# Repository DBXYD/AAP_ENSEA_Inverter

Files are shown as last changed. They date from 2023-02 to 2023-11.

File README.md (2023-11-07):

# ENSEA - Projet Onduleur Triphasé didactique, 60V, 10A
- Rédaction : Nicolas Papazoglou, Alexis Martin,
- Desgin et Réalisation : Nicolas Papazoglou, Alexis Martin, Patricia Kittel,
- Conseils : Pierre Toussaint.

# Présentation du projet

## Motivations
Dans le cadre de la formation des étudiants de l'ENSEA, les professeurs ont ressenti le besoin de créer une maquette pédagogique pour plusieurs raisons : 
* De nombreuses pannes récurentes sur les maquettes existantes,
* Réparations chronophages voir impossibles,
* L'ensemble du matériel est caché des étudiants, ils ne peuvent pas voir l'intérieur, le routage de la carte et les composants,
* Le coût de l'ensemble du matériel acheté est important.

## Objectifs
* Réalisation d'une maquette fiable pour les TPs d’électrotechnique et automatique : Gain en temps et en autonomie pour les étudiants,
* Feedback automatique en fonction des erreurs détectées : Gain en autonomie pour les étudiants, possibilité de travail hors séance sans
supervision d’un professeur,
* Projet open-source (disponible sur github),
* Compréhension globale possible par les étudiants, application de l’ensemble de leurs cours dans une maquette,
* Création modulaire, réutilisable dans d’autres cours/projets,
* Evolution possible à d’autres enseignements (buck/boost, 4Q, brushless, moteurs synchrones, asservissement, etc...),
* Maintenance facile et rapide

## Cahier des charges
* Onduleur triphasé 60V / 15A,
* Protections surtensions et surintensités,
* Commande de mise sous tension,
* Pilotage par liaison UART over USB,
* Utilisable en commande “brushless” : entrées position “hall” ,
* Utilisable en commande vectorielle ou MCC : entrée position “encoder”,
* Protection alimentation non réversible : module “freinage”,
* Vérification automatique des temps morts,
* Mesure de courants (hall) dans les 3 phases + entrée,
* Mesure de tension dans les 3 phases + entrée,
* Alimentation externe secteur,
* Affichage erreurs, intensité PWM (affiche externe),
* Sorties mesures de courants et PWMs,
* Boitier,
* Tenue thermique,
* Isolation galvanique.

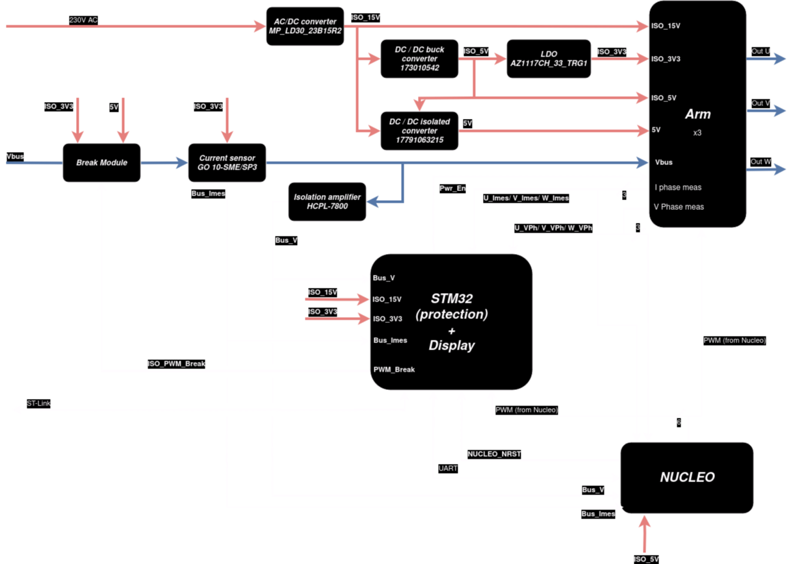
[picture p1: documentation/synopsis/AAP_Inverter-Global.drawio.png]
synopsis


# Guide d'utilisation

# Guide du développeur
La majorité des signaux sont disponibles sur les connecteurs morpho au format des cartes Nucleo-64.
Sur la base des cartes Nucleo, les connecteurs répérés CN7 et CN10 sont disponibles pour intégrer une carte custom.

## Connecteurs
### Connecteur CN7
| Type           | Label         | Pin number | Pin number | Label         | Type           |
|----------------|---------------|------------|------------|---------------|----------------|
| Digital Output | UART_TX_STM32 | 1          | 2          | UART_RX_STM32 | Digital Input  |
|                | N.C.          | 3          | 4          | NRST_STM32    | Digital Output |
|                | N.C.          | 5          | 6          | 5V            | Power Input    |
|                | N.C.          | 7          | 8          | GND           | Power Input    |
|                | N.C.          | 9          | 10         | N.C           |                |
|                | N.C.          | 11         | 12         | N.C           |                |
|                | N.C.          | 13         | 14         | N.C.          |                |
|                | N.C.          | 15         | 16         | N.C.          |                |
|                | N.C.          | 17         | 18         | N.C.          |                |
| Power Input    | GND           | 19         | 20         | GND           | Power Input    |
|                | N.C.          | 21         | 22         | GND           | Power Input    |
|                | N.C.          | 23         | 24         | N.C.          |                |
|                | N.C.          | 25         | 26         | N.C.          |                |
|                | N.C.          | 27         | 28         | Bus_V         | Analog Input   |
|                | N.C.          | 29         | 30         | U_Imes        | Analog Input   |
|                | N.C.          | 31         | 32         | Enc_B         | Digital Input  |
|                | N.C.          | 33         | 34         | W_Imes        | Analog Input   |
| Analog Input   | Bus_Imes      | 35         | 36         | W_Vph         | Analog Input   |
| Analog Input   | V_Vph         | 37         | 38         | U_Vph         | Analog Input   |

### Connecteur CN10
| Type           | Label         | Pin number |            | Label         | Type           |
|----------------|---------------|------------|------------|---------------|----------------|
|                | N.C.          | 1          | 2          | Enc_Z         | Digital Input  |
|                | N.C.          | 3          | 4          | N.C.          |                |
|                | N.C.          | 5          | 6          | N.C.          |                |
|                | N.C.          | 7          | 8          | N.C.          |                |
| Power Input    | GND           | 9          | 10         | N.C.          |                |
|                | N.C.          | 11         | 12         | N.C.          |                |
| Digital Input  | Enc_A         | 13         | 14         | N.C.          |                |
|                | N.C.          | 15         | 16         | N.C.          |                |
|                | N.C.          | 17         | 18         | N.C.          |                |
|                | N.C.          | 19         | 20         | GND           | Power Input    |
| Output         | V_PWM_H       | 21         | 22         | N.C.          |                |
| Output         | U_PWM_H       | 23         | 24         | V_Imes        | Analog Input   |
|                | N.C.          | 25         | 26         | W_PWM_L       | Output         |
|                | N.C.          | 27         | 28         | V_PWM_L       | Output         |
|                | N.C.          | 29         | 30         | U_PWM_L       | Output         |
|                | N.C.          | 31         | 32         | GND           | Power Input    |
| Output         | W_PWM_H       | 33         | 34         | N.C.          |                |
|                | N.C.          | 35         | 36         | N.C.          |                |
|                | N.C.          | 37         | 38         | N.C.          |                |

## Input / Output labels

### Communication avec le micro-controleur présent sur la carte-mère
* UART_TX_STM32 : UART vers le micro-controleur
* UART_RX_STM32 : UART depuis le micro-controleur
* NRST_STM32 : signal pour faire un reset du micro-controleur de la carte

### Communication avec le module encodeur
* Enc_A : entrée du signal A de l'encodeur
* Enc_B : entrée du signal B de l'encodeur
* Enc_Z : entrée du signal Z de l'encodeur

### Mesure de tension
* Bus_V : mesure de la tension du bus d'alimentation
* U_Vph : mesure de la tension de la sortie U (entre les 2 transistors)
* V_Vph : mesure de la tension de la sortie V (entre les 2 transistors)
* W_Vph : mesure de la tension de la sortie W (entre les 2 transistors)

### Mesure de courant
* Bus_Imes : mesure de courant du bus d'alimentation
* U_Imes
* V_Imes
* W_Imes

### Génération de PWM
* U_PWM_H
* U_PWM_L
* V_PWM_H
* V_PWM_L
* W_PWM_H
* W_PWM_L

# FAQ

# Pannes courantes 
## Dysfonctionnement des Mosfet
Plusieurs causes peuvent causer la destruction des transistors : 
* Non respect des temps mort,
* Commande provocant une freinage trop important : retour du courant chargeant les condensateurs sur le bus d'alimentation. Ceci provoque la montée en tension du bus au-delà des spécifications des transistor de puissance

Détection de la panne : 
* Débrancher l'ensemble des câbles de la maquette, et le cas échéant, attendre que les condensateurs du bus d'alimentation soient totalement vides.
* A l'aide d'un multimètre, en mode diode, tester la continuité entre :
  - Entre la sortie U et le bus d'alimentation (Q202)
  - Entre la sortie U et la masse (Q203)
  - Entre la sortie V et le bus d'alimentation (Q302)
  - Entre la sortie V et la masse (Q303)
  - Entre la sortie W et le bus d'alimentation (Q402)
  - Entre la sortie W et la masse (Q403)
* Le fonctionnement normal est l'absence de continuité électrique. Dans le cas d'une continuité, le transistor en question est HS, il doit donc être changé.

# Composants
* Drivers de Mosfet/optocoupleur : HCPL-315J, Optocoupleurs sortie logique 0.5A IGBT Gate Drive [link](https://www.mouser.fr/ProductDetail/Broadcom-Avago/HCPL-315J?qs=s%252BgfxR24RQ4lntGToXJAvA%3D%3D)
* Transistor MOSFET : IRF540NPBF, MOSFET de puissance, Canal N, 100 V, 33 A, 0.044 ohm, TO-220AB, Traversant [Link](https://fr.farnell.com/infineon/irf540npbf/transistor-mosfet-canal-n-to220/dp/8648298?st=irf540n)
* Capteur de Courant : GO 10-SME/SP3, Capteur de courant, 300 kHz, SOIC, 8 Broche(s), 3.135 V, 3.465 V [Link](https://fr.farnell.com/lem/go-10-sme-sp3/capteur-courant-300khz-soic-8/dp/3796461?st=GO%2010-SME/SP3)
* Power supply : MP-LD30-23B15R2 - Alimentation montage PCB AC/DC (PSU), ITE, Équipements Ménagers et Transformateurs, 1 sortie [link](https://fr.farnell.com/multicomp-pro/mp-ld30-23b15r2/power-supply-ac-dc-15v-2a/dp/3780527)
* Power regulator : Input : 5V DC, Output : 3.3V DC, AZ1117CH-3.3TRG1 - LDO, FIXE, 3,3V, 0.8A, -20 A 125°C [link](https://fr.farnell.com/diodes-inc/az1117ch-3-3trg1/ldo-fixe-3-3v-0-8a-20-a-125-c/dp/3483073RL)
* Alimentation 15V/400mA isolé : MPRB2415S-6W - Conv. DC/DC, montage traversant isolé, ITE, 4:1, 6 W, 1 sortie, 15 V, 400 mA [link](https://fr.farnell.com/multicomp-pro/mprb2415s-6w/convertisseur-dc-dc-15v-0-4a/dp/3652723)
* Alimentation 5V/200mA isolé : 17791063215 - MagI³C-VISM Variable Isolated SIP Module, [Link](https://www.we-online.com/components/products/datasheet/17791063215.pdf)
* Connector : PX0580/PC Connecteur de puissance IEC, Entrée IEC C14, 10 A, 250 VAC, Traversant [link](https://fr.farnell.com/bulgin/px0580-pc/embase-iec-c14-carte-proto-10a/dp/313853)
* Screen : MDOB128064XV-YI - OLED graphique, 128 x 64 pixels, Jaune sur noir, 3.3V, I2C, 35.5mm x 32mm, -40 °C [Link](https://fr.farnell.com/midas/mdob128064xv-yi/afficheur-oled-cob-128-x-64-pix/dp/3407293)
* Break resistor : 162-3488 - Résistance à montage sur châssis Aluminium, 5Ω 100W ±1% [Link](https://fr.rs-online.com/web/p/resistances-a-montage-sur-chassis/1623488)
* Break schottky : VS-15TQ060S-M3 - Redresseur Schottky, 60 V, 15 A, Une, TO-263AB, 3 Broche(s), 620 mV [Link](https://fr.farnell.com/vishay/vs-15tq060s-m3/diode-schottky-simple-60v-to263ab/dp/2909608?ost=2909608)

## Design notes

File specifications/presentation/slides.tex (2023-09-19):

%\documentclass[french]{beamer}
\documentclass[aspectratio=169]{beamer}
\usepackage[utf8]{inputenc}
\usepackage[T1]{fontenc}
\usepackage{lmodern}
\usepackage{amsmath, amssymb}
\usepackage{babel}

\usepackage{eurosym}
%\usepackage{unicode-math}
\setbeamertemplate{footline}[frame number]
\def\checkmark{\tikz\fill[scale=0.4](0,.35) -- (.25,0) -- (1,.7) -- (.25,.15) -- cycle;} 
\definecolor{rouge}{HTML}{DD0000}

%Pour le TITLEPAGE

\title{Appel à projet - Présentation}
\subtitle{\today}
\date{}
\author[N.P. - A.M. - P.T.]{Nicolas Papazoglou, Alexis Martin \& Pierre Toussaint}
\institute[ENSEA]{ENSEA}

\usetheme{ensea}  

\begin{document}

\begin{frame}
	\titlepage
\end{frame}

\begin{frame}{Rappel}
\begin{minipage}{0.49\textwidth}
	\begin{itemize}
		\item Porteurs du projet : Nicolas Papazoglou, Alexis Martin, Pierre Toussaint,
		\item Demande budgétaire : 64 HETD, 
		\item Budget (DEE) : 400-500\euro/maquette,
		\item Activités concernées : enseignements d'électrotechnique et d'automatique.
	\end{itemize}
\end{minipage}
\begin{minipage}{0.49\textwidth}
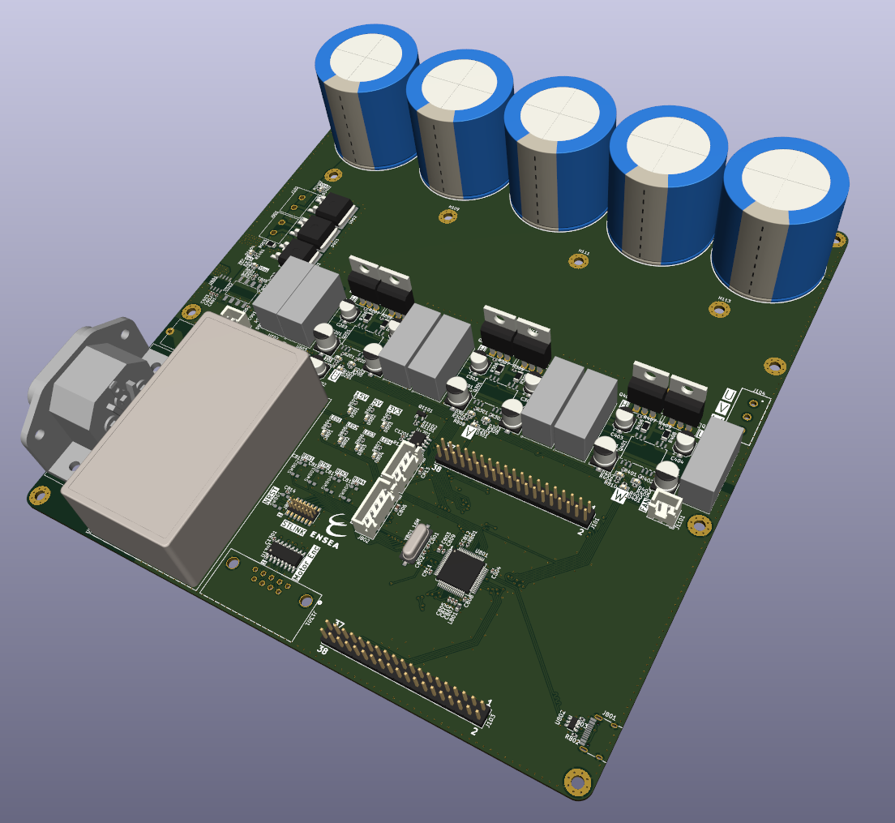
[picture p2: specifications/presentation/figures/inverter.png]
	 
\end{minipage}
\center \href{https://github.com/DBXYD/AAP_ENSEA_Inverter}{Lien github}
\end{frame}

%********************** OBJECTIFS ******************************
\begin{frame}{Contexte}
\begin{itemize}
	\item Maquette de TP : onduleur triphasé,
	\item TP en 3eme année (Enseignements d'électrotechnique et d'automatique) : 
	\begin{itemize}
	\item [ESE\_3745] Actionneur et automatique appliquée
	\item [MSC\_3805] Systèmes d'Acquision et de commande
	\end{itemize}
	\item 12 maquettes obsolète Powermodule MC1L 3-Phase (Microchip) : 
	\item Pannes récurentes :
	\begin{itemize}
		\item Perte de temps pour les étudiants,
		\item Recherche de panne et réparation par les professeurs,
		\item Boite noire pour les étudiants.		
	\end{itemize}
\end{itemize}
\end{frame}

\begin{frame}{Objectif : Réalisation maquette pédagogique}
	Objectifs : 
	\begin{enumerate}
		\item Une maquette fiable pour les TPs d'électrotechnique et automatique \\
		$\rightarrow$ Gain en temps et en autonomie pour les étudiants, \checkmark
		\item Feedback automatique en fonction des erreurs détectées, \\
		$\rightarrow$ Gain en autonomie pour les étudiants, possibilité de travail hors séance sans supervision d'un professeur,
		\item Projet open-source (disponible sur \href{https://github.com/DBXYD/AAP_ENSEA_Inverter}{github}), \checkmark
		\item Compréhension globale possible par les étudiants, application de l'ensemble de leurs cours dans une maquette, \checkmark
		\item Création modulaire, réutilisable dans d'autres cours/projets,  \checkmark
		\item Evolution possible à d'autres enseignements (buck/boost, 4Q, brushless, moteurs synchrones, asservissement, etc...), \checkmark
		\item Maintenance facile et rapide. \checkmark
	\end{enumerate}
\end{frame}

\begin{frame}{Bilan}
\begin{enumerate}
	\item Cahier des charges \checkmark,
	\item Schéma d'architecture \checkmark,
	\item Choix des composants \checkmark,
	\item Prototypage et tests unitaires électriques \checkmark,
	\item Réalisation software et tests complets (50\%),
	\item Réalisation mécanique (boitier) (50\%),
	\item Documentation (\href{https://github.com/DBXYD/AAP_ENSEA_Inverter}{github}). (80\%)
\end{enumerate}
\pause
Remarque :\begin{itemize}
	\item Coût : 300\euro/maquette,
	\item 8 cartes en fabrication dans l'immédiat
	\item Beaucoup de composants gratuits
\end{itemize}	
\end{frame}

\begin{frame}{Schematic}
\begin{center}
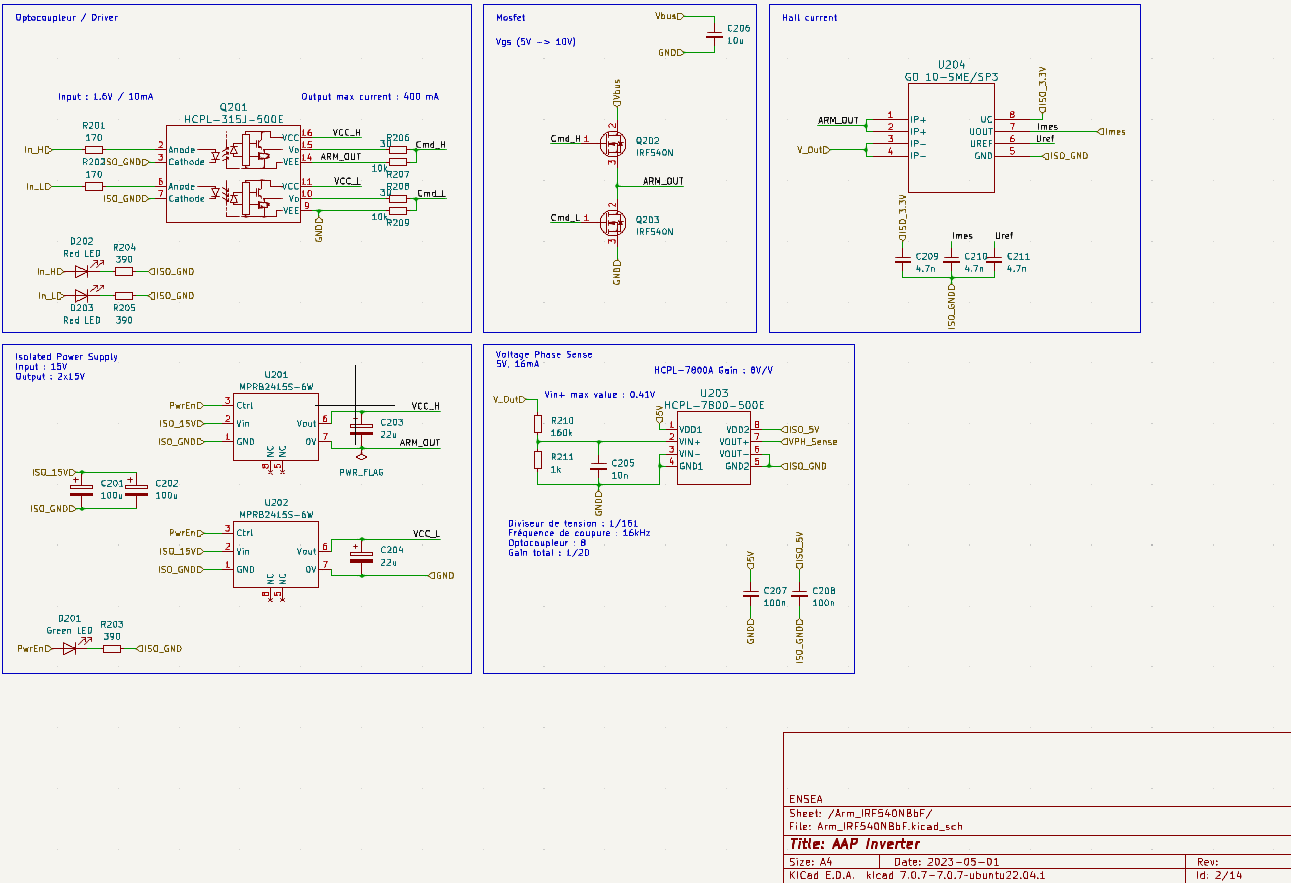
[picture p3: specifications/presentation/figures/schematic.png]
	 
\end{center}
\end{frame}

\begin{frame}{PCB}
\begin{minipage}{0.49\textwidth}
\begin{center}
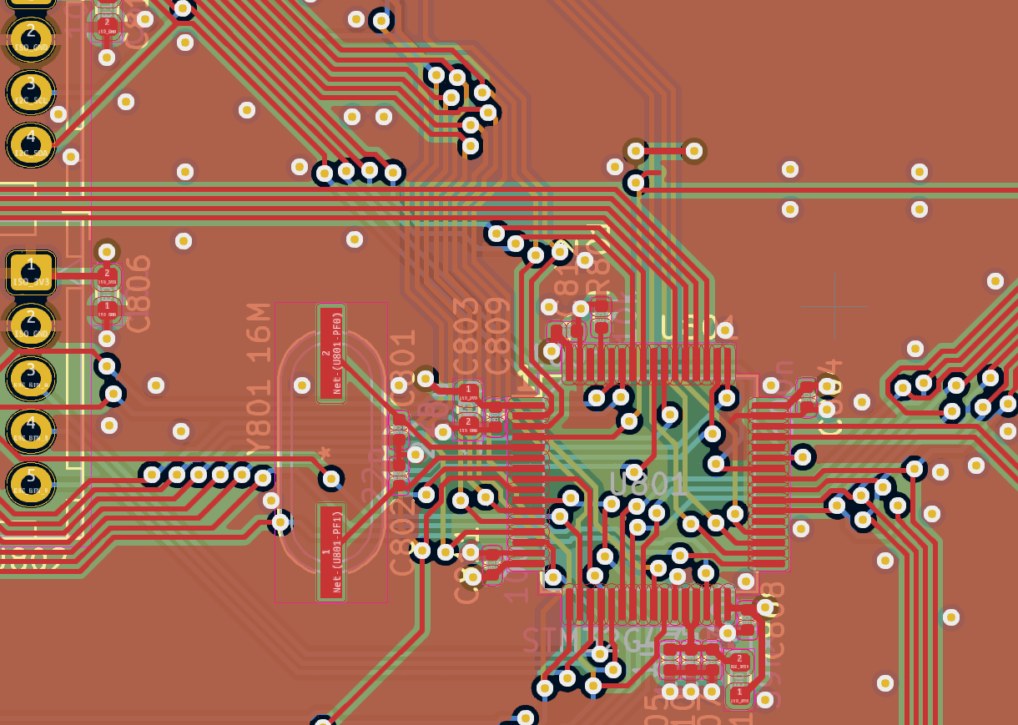
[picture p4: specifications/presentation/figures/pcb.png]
	 
\end{center}
\end{minipage}
\begin{minipage}{0.49\textwidth}
\begin{itemize}
	\item 242 composants (60 différents),
	\item 2000 segments de pistes,
	\item 906 pads
	\item 225 signaux
\end{itemize}
\end{minipage}
\end{frame}

\begin{frame}{La suite}
\begin{minipage}{0.39\textwidth}
\begin{center}
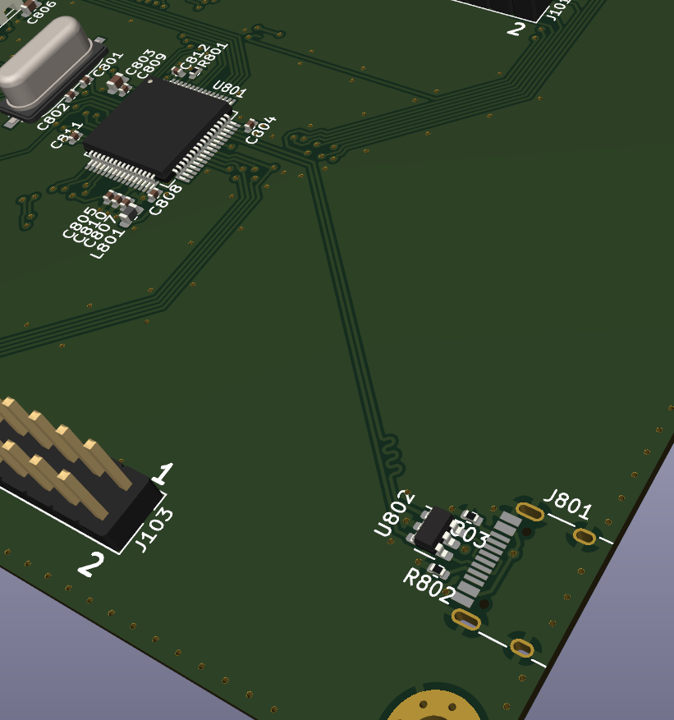
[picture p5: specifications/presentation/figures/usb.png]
	 
\end{center}
\end{minipage}
\begin{minipage}{0.59\textwidth}
Idée 1 : 
\begin{itemize}
	\item Connexion usb fonctionnelle
	\item Possibilité de récupérer toutes les données internes
	\item Programme et interface (Python) pour afficher de façon didactique l'état du moteur
\end{itemize}
Idée 2 : 
\begin{itemize}
	\item Possibilité de TP de puissance à distance
\end{itemize}
Idée 3 : 
\begin{itemize}
	\item Portage de ce projet sur d'autres cours 
	\item Carte fille différente (remplacement de la Nucléo)
\end{itemize}
\end{minipage}
\end{frame}

\end{document}

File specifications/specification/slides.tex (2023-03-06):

%\documentclass[french]{beamer}
\documentclass[aspectratio=169]{beamer}
\usepackage[utf8]{inputenc}
\usepackage[T1]{fontenc}
\usepackage{lmodern}
\usepackage{amsmath, amssymb}
\usepackage{babel}

\usepackage{eurosym}
%\usepackage{unicode-math}
\setbeamertemplate{footline}[frame number]

\definecolor{rouge}{HTML}{DD0000}

%Pour le TITLEPAGE

\title{Appel à projet}
\subtitle{Mardi 7 mars 2023}
\date{}
\author[N.P. - A.M. - P.T.]{Nicolas Papazoglou, Alexis Martin \& Pierre Toussaint}
\institute[ENSEA]{ENSEA}

\usetheme{ensea}  

\AtBeginSection[]
{
	\begin{frame}{Plan}
		\tableofcontents[currentsection]
	\end{frame}
}

\AtBeginSubsection[]
{
   \begin{frame}
    	\tableofcontents[currentsection,currentsubsection]
   \end{frame}
}

\begin{document}

\begin{frame}
	\titlepage
\end{frame}

\begin{frame}{Appel à projet}
\begin{minipage}{0.49\textwidth}
	\begin{itemize}
		\item Porteurs du projet : Alexis Martin, Nicolas Papazoglou, Pierre Toussaint,
		\item Demande budgétaire : 64 HETD,
		\item Budget (DEE) : 400-500\euro/maquette,
		\item Activités concernées : enseignements d'électrotechnique et d'automatique.
	\end{itemize}
\end{minipage}
\begin{minipage}{0.49\textwidth}
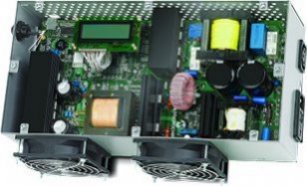
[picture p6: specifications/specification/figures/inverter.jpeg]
	 
\end{minipage}
\center \href{https://github.com/DBXYD/AAP_ENSEA_Inverter}{Lien github}
\end{frame}

%********************** OBJECTIFS ******************************
\begin{frame}{Contexte}
\begin{itemize}
	\item Maquette de TP : onduleur triphasé,
	\item TP en 3eme année (Enseignements d'électrotechnique et d'automatique) : 
	\begin{itemize}
	\item [AEI\_3121] Commande numérique directe de dispositifs
	\item [ESE\_3745] Actionneur et automatique appliquée
	\item [MSC\_3805] Systèmes d'Acquision et de commande
	\end{itemize}
	\item 12 maquettes obsolète Powermodule MC1L 3-Phase (Microchip) : 
	\item Pannes récurentes :
	\begin{itemize}
		\item Perte de temps pour les étudiants,
		\item Recherche de panne et réparation par les professeurs,
		\item Boite noire pour les étudiants.		
	\end{itemize}
\end{itemize}
\end{frame}

\begin{frame}{Objectif : Réalisation maquette pédagogique}
	Objectifs : 
	\begin{enumerate}
		\item Une maquette fiable pour les TPs d'électrotechnique et automatique \\
		$\rightarrow$ Gain en temps et en autonomie pour les étudiants,
		\item Feedback automatique en fonction des erreurs détectées, \\
		$\rightarrow$ Gain en autonomie pour les étudiants, possibilité de travail hors séance sans supervision d'un professeur,
		\item Projet open-source (disponible sur \href{https://github.com/DBXYD/AAP_ENSEA_Inverter}{github}),
		\item Compréhension globale possible par les étudiants, application de l'ensemble de leurs cours dans une maquette,
		\item Création modulaire, réutilisable dans d'autres cours/projets, 
		\item Evolution possible à d'autres enseignements (buck/boost, 4Q, brushless, moteurs synchrones, asservissement, etc...),
		\item Maintenance facile et rapide.
	\end{enumerate}
\end{frame}

\begin{frame}{Travail à effectuer}
\begin{enumerate}
	\item Cahier des charges (déjà effectué),
	\item Schéma d'architecture (déjà effectué),
	\item Choix des composants (disponibles et actuels pour une maintenibilité la plus longue possible),
	\item Prototypage et tests unitaires électriques,
	\item Réalisation software et tests complets,
	\item Réalisation mécanique (boitier),
	\item Intégration complète,
	\item Documentation (\href{https://github.com/DBXYD/AAP_ENSEA_Inverter}{github}).
\end{enumerate}
\end{frame}

\begin{frame}{Travail déjà effectué : Cahier des charges}
\begin{itemize}
	\item Onduleur triphasé 60V / 15A,
	\item Protections surtensions et surintensités,
	\item Commande de mise sous tension,
	\item Commande UART,
	\item Utilisable en commande ``brushless'' :  entrées position ``hall'' ,
	\item Utilisable en commande vectorielle ou MCC : entrée position ``encoder'',
	\item Protection alimentation non réversible : module ``freinage'',
	\item Vérification des temps morts,
	\item Mesure de courants (hall) dans les 3 phases + entrée,
	\item Mesure de tension dans les 3 phases + entrée,
	\item Alimentation externe secteur,
	\item Affichage erreurs, intensité PWM (affiche externe),
	\item Sorties mesures de courants et PWMs,
	\item Boitier,
	\item Tenue thermique,
	\item Isolation galvanique.
\end{itemize}
\end{frame}

\begin{frame}{Travail déjà effectué : Schéma d'architecture}
 
\end{frame}

\begin{frame}{Dead-line et rémunération}
\begin{itemize}
	\item Prototype fonctionnel pour la rentrée de septembre 2023,
	\item Rémunération demandée : 64 HETD.
\end{itemize}

\end{frame}

\end{document}

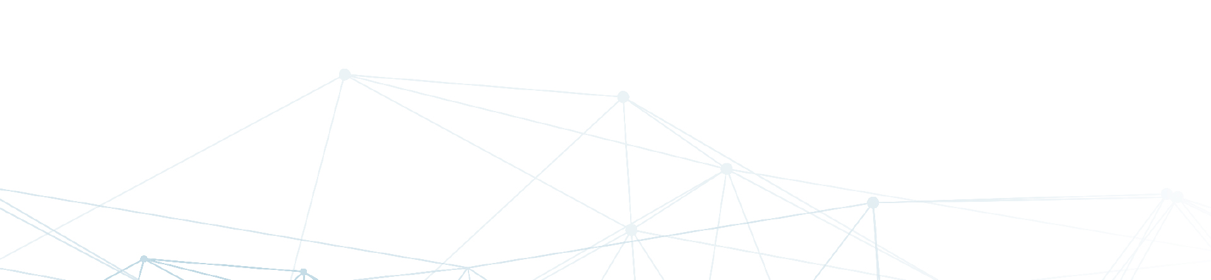
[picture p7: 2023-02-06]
specifications/presentation/template/Powerpoint ENSEA 2021 16-9 p10.jpg

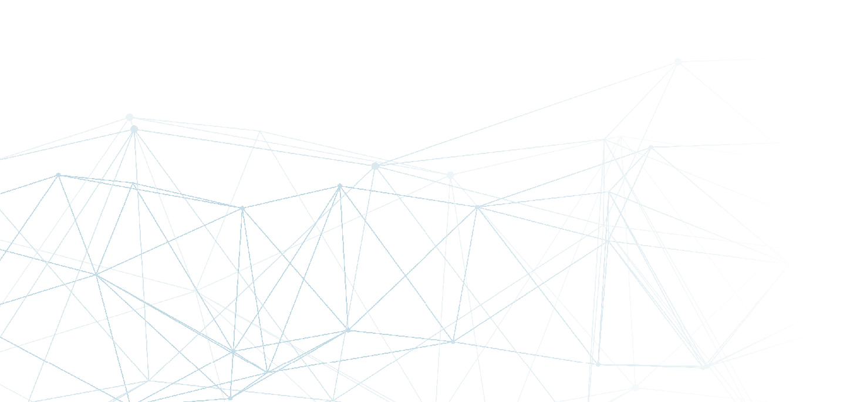
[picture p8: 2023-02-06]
specifications/presentation/template/Powerpoint ENSEA 2021 16-9 p2.jpg

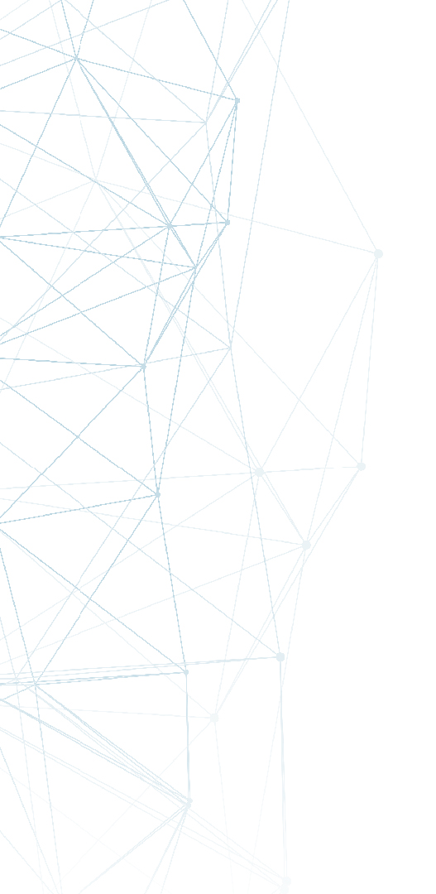
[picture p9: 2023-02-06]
specifications/specification/template/Powerpoint ENSEA 2021 16-9 p5.jpg

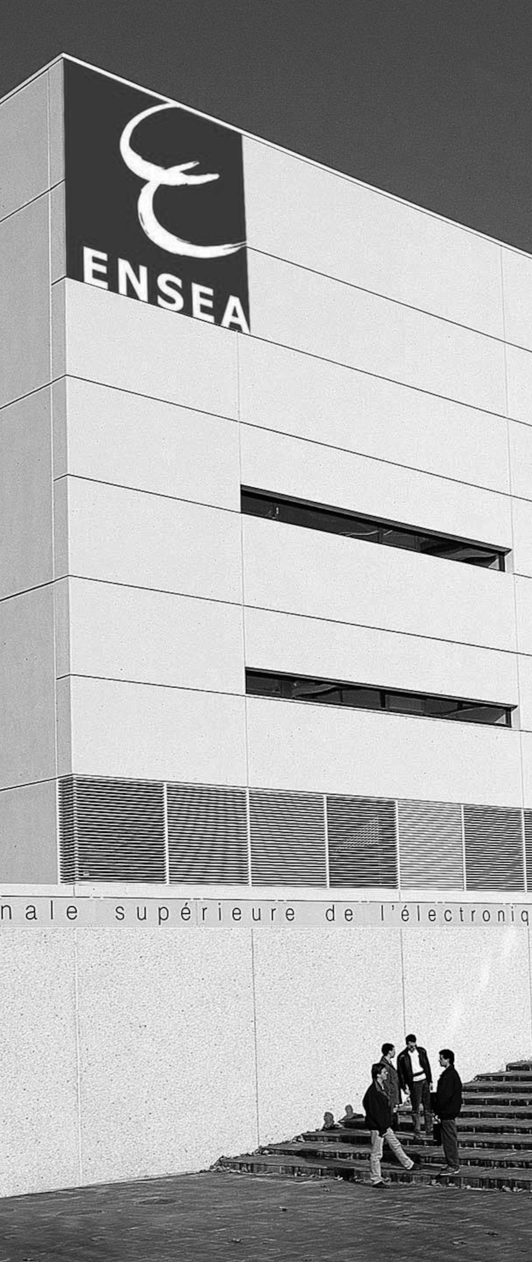
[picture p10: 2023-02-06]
specifications/specification/template/ensea-batiment.png

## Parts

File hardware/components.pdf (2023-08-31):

Sheet1

Page 1

Qty/pcs Total Stock | Fournisseurs | Reference(s) Value | LibPart | Footprint
6 | 60 | C201, C202, C3100u | Device:C_Polarized | Capacitor_SMD:CP_Elec_6.3x7.7
7 | 70 | C203, C204, C322u | Device:C_Polarized | Capacitor_SMD:CP_Elec_5x5.4
4 | 40 | C205, C305, C410n | Device:C_Small | Capacitor_SMD:C_0402_1005Metric_Pad0.74x0.62mm_HandSolder
3 | 30 | C206, C306, C410u | Device:C_Small | Capacitor_SMD:C_2220_5650Metric
24 | 240 | C207, C208, C30100n | Device:C_Small | Capacitor_SMD:C_0402_1005Metric_Pad0.74x0.62mm_HandSolder
12 | 120 | C209, C210, C24.7n | Device:C_Small | Capacitor_SMD:C_0402_1005Metric_Pad0.74x0.62mm_HandSolder
1 | 10 | | C501 | 10u | Device:C_Polarized | Capacitor_SMD:CP_Elec_4x5.4
2 | 20 | | C801, C802 | 18p | Device:C_Small | Capacitor_SMD:C_0402_1005Metric_Pad0.74x0.62mm_HandSolder
3 | 30 | C803, C806, C810u | Device:C_Small | Capacitor_SMD:C_0603_1608Metric_Pad1.08x0.95mm_HandSolder
2 | 20 | | C805, C903 | 1u | Device:C_Small | Capacitor_SMD:C_0402_1005Metric_Pad0.74x0.62mm_HandSolder
1 | 10 | | C904 | 1n | Device:C_Small | Capacitor_SMD:C_0402_1005Metric_Pad0.74x0.62mm_HandSolder
5 | 50 | C1001, C1002, 1.5m | Device:C_Polarized | Capacitor_THT:CP_Radial_D35.0mm_P10.00mm_SnapIn
3 | 30 | Wurth | D201, D301, D4Green LED | Device:LED | LED_SMD:LED_0603_1608Metric_Pad1.05x0.95mm_HandSolder
9 | 90 | Wurth | D202, D203, D3Red LED | Device:LED | LED_SMD:LED_0603_1608Metric_Pad1.05x0.95mm_HandSolder
4 | 40 | Wurth | D801, D802, D8Blue LED | Device:LED | LED_SMD:LED_0603_1608Metric_Pad1.05x0.95mm_HandSolder
1 | 10 | Wurth | D901 | Red | Device:LED_Small | LED_SMD:LED_0603_1608Metric_Pad1.05x0.95mm_HandSolder
2 | 20 | | D902, D903 | VS-15TQ060S-M3 | Device:D_Schottky | Package_TO_SOT_SMD:TO-263-2
1 | 10 | Wurth | F501 | Fuse | Device:Fuse | Custom:0031.8201
8 | 80 | - | H101, H102, H1MountingHole_Pad | Mechanical:MountingHole_Pad | MountingHole:MountingHole_3.2mm_M3_Pad_Via
2 | 20 | J101, J103 | Conn_02x19_Odd_Even | Connector_Generic:Conn_02x19_Odd_Even Connector_PinHeader_2.54mm:PinHeader_2x19_P2.54mm_Vertical
2 | 20 | Wurth | J102, J901 | Conn_01x02 | Connector_Generic:Conn_01x02 | Custom:691311500102
1 | 10 | Wurth | J104 | Conn_01x03 | Connector_Generic:Conn_01x03 | Custom:691311500103
1 | 10 | | J501 | PX0580-PC-12132 | PX0580-PC-12132:PX0580-PC-12132 | Custom:PX0580-PC-12132
1 | 10 | Wurth | J801 | USB_C_Receptacle_USB2.0 | Connector:USB_C_Receptacle_USB2.0 | Connector_USB:USB_C_Receptacle_HRO_TYPE-C-31-M-12
1 | 10 | | J802 | Conn_01x05 | Connector_Generic:Conn_01x05 | Connector_JST:JST_XH_B5B-XH-A_1x05_P2.50mm_Vertical
1 | 10 | | J803 | Conn_ST_STDC14 | Connector:Conn_ST_STDC14 | Connector_PinHeader_1.27mm:PinHeader_2x07_P1.27mm_Vertical_SMD
1 | 10 | | J804 | Conn_01x04 | Connector_Generic:Conn_01x04 | Connector_JST:JST_XH_B4B-XH-A_1x04_P2.50mm_Vertical
2 | 20 | | J1101, J1102 | Conn_01x02 | Connector_Generic:Conn_01x02 | Connector_JST:JST_XH_B2B-XH-A_1x02_P2.50mm_Vertical
1 | 10 | Wurth | J1301 | DE9_Receptacle_MountingHoles | Connector:DE9_Receptacle_MountingHoles | Custom:618009233821
1 | 10 | | J1302 | Conn_01x03 | Connector_Generic:Conn_01x03 | Connector_PinHeader_2.54mm:PinHeader_1x03_P2.54mm_Vertical
1 | 10 | | L801 | 39n | Device:L_Small | Inductor_SMD:L_0603_1608Metric_Pad1.05x0.95mm_HandSolder
3 | 30 | Q201, Q301, Q4HCPL-315J-500E | Custom:HCPL-315J-500E | Custom:SO-16_HCPL-315J_BRA
6 | 60 | Q202, Q203, Q3IRF540N | Transistor_FET:IRF540N | Package_TO_SOT_THT:TO-220-3_Vertical
1 | 10 | | Q901 | BUK9637-100E | Transistor_FET:IRFS4229 | Package_TO_SOT_SMD:TO-263-2
1 | 10 | | Q1101 | SQ2310ES | Device:Q_NMOS_GSD | Package_TO_SOT_SMD:SOT-23
6 | 60 | R201, R202, R3170 | Device:R_Small | Resistor_SMD:R_0402_1005Metric_Pad0.72x0.64mm_HandSolder
15 | 150 | R203, R204, R20390 | Device:R_Small | Resistor_SMD:R_0402_1005Metric_Pad0.72x0.64mm_HandSolder
6 | 60 | R206, R208, R330 | Device:R_Small | Resistor_SMD:R_1206_3216Metric_Pad1.30x1.75mm_HandSolder
6 | 60 | R207, R209, R310k | Device:R_Small | Resistor_SMD:R_0402_1005Metric
4 | 40 | R210, R310, R4160k | Device:R_Small | Resistor_SMD:R_0402_1005Metric_Pad0.72x0.64mm_HandSolder
4 | 40 | R211, R311, R41k | Device:R_Small | Resistor_SMD:R_0402_1005Metric_Pad0.72x0.64mm_HandSolder
1 | 10 | | R501 | 2k7 | Device:R_Small | Resistor_SMD:R_0402_1005Metric_Pad0.72x0.64mm_HandSolder
1 | 10 | | R502 | 680 | Device:R_Small | Resistor_SMD:R_0402_1005Metric_Pad0.72x0.64mm_HandSolder
1 | 10 | | R701 | 27k | Device:R_Small | Resistor_SMD:R_0402_1005Metric_Pad0.72x0.64mm_HandSolder
2 | 20 | | R801, R902 | 10k | Device:R_Small | Resistor_SMD:R_0402_1005Metric_Pad0.72x0.64mm_HandSolder
2 | 20 | | R802, R803 | 5.1k | Device:R_Small | Resistor_SMD:R_0402_1005Metric_Pad0.72x0.64mm_HandSolder
1 | 10 | | R903 | 5 | Device:R_Small | Resistor_SMD:R_1206_3216Metric_Pad1.30x1.75mm_HandSolder
1 | 10 | | R1101 | 22 | Device:R_Small_US | Resistor_SMD:R_0402_1005Metric_Pad0.72x0.64mm_HandSolder
1 | 10 | | R1102 | 10k | Device:R_Small_US | Resistor_SMD:R_0402_1005Metric_Pad0.72x0.64mm_HandSolder
1 | 10 | | R1201 | 200 | Device:R_Small | Resistor_SMD:R_0402_1005Metric_Pad0.72x0.64mm_HandSolder
5 | 50 | Wurth | SW801, SW802,SW_Push | Switch:SW_Push | Custom:435451019820
3 | 30 | U201, U301, U4MPRB2415S-6W | Custom:MPRB2415S-6W | Custom:MPRB2415S
3 | 30 | U202, U302, U4MPRB2415S-6W | :MPRB2415S-6W_1 | Custom:MPRB2415S
4 | 40 | U203, U303, U4HCPL-7800-500E | Custom:HCPL-7800-500E | Custom:DIP-8 Gull Wing
55 | 4 | U204, U304, U4GO 10-SME/SP3 | Custom:GO_10-SME | Custom:SOIC8-GO-SME&slash_SP3_LEM
56 | 1 | | U501 | MP-LD30-23B12R2 | MP-LD30-23B15R2:MP-LD30-23B12R2 | Custom:MP-LD30-23B15R2
57 | 1 | U502 | 173010542 Custom:173010542 | Custom:173010578
58 | 1 | | U503 | AZ1117-3.3 | Regulator_Linear:AZ1117-3.3 | Package_TO_SOT_SMD:SOT-223-3_TabPin2
59 | 1 | U701 | 17791063215 Custom:17791063215 | Custom:17791063215
60 | 1 | | U801 | STM32G474RETx | MCU_ST_STM32G4:STM32G474RETx | Package_QFP:LQFP-64_10x10mm_P0.5mm
61 | 1 | | U802 | USBLC6-2SC6 | Power_Protection:USBLC6-2SC6 | Package_TO_SOT_SMD:SOT-23-6
62 | 1 | | U901 | ACPL-077L | Custom:ACPL-077L | Package_SO:SO-8_3.9x4.9mm_P1.27mm
63 | 1 | | U902 | TC1412 | Custom:TC1412 | Package_SO:SOIC-8_3.9x4.9mm_P1.27mm
64 | 1 | | U1201 | TCN75A | Custom:TCN75A | Package_SO:SOIC-8_3.9x4.9mm_P1.27mm
65 | 1 | | U1301 | MAX3097ECSE+ | Custom:MAX3097ECSE+ | Package_SO:SOIC-16_3.9x9.9mm_P1.27mm
66 | 1 | | Y801 | 16M | Device:Crystal | Custom:ABLS-7.3728MHZ-CL-RESR-A-1-G-F

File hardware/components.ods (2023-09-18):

On board
Reference | Value | Footprint | Datasheet | Fournisseur | MFR | Ref | Qty | Total | Stock | Diff | Commande
C1001-C1005 | 1.5m | Capacitor_THT:CP_Radial_D35.0mm_P10.00mm_SnapIn | ~ | Wurth | 861 011 086 027 |  | 5 | 50 | 95 | 0 | 0
C201, C202, C301, C302, C401, C402 | 100u | Capacitor_SMD:CP_Elec_6.3x7.7 | ~ | Wurth | 865 060 445 005 |  | 6 | 60 | 100 | 0 | 0
C203, C204, C303, C304, C403, C404, C502 | 22u | Capacitor_SMD:CP_Elec_5x5.4 | ~ | Wurth | 865 060 442 002 |  | 7 | 70 | 100 | 0 | 0
C205, C305, C405, C604 | 10n | Capacitor_SMD:C_0402_1005Metric | ~ | Wurth | 885 012 205 050 |  | 4 | 40 | 100 | 0 | 0
C206, C306, C406 | 10u | Capacitor_SMD:C_2220_5650Metric | https://www.we-online.com/components/products/datasheet/885012214001.pdf | Wurth | 885 012 214 001 |  | 3 | 30 | 0 | 30 | 50
C207, C208, C307, C308, C407, C408, C605, C606, C804, C807-C812, C814-C818, C901, C902, C1201, C1301 | 100n | Capacitor_SMD:C_0402_1005Metric | ~ | Wurth | 885 012 105 018 |  | 24 | 240 | 1000 | 0 | 0
C209-C211, C309-C311, C409-C411, C601-C603 | 4.7n | Capacitor_SMD:C_0402_1005Metric | ~ | Wurth | 885 012 205 048 |  | 12 | 120 | 100 | 20 | 100
C501 | 10u | Capacitor_SMD:CP_Elec_4x5.4 | ~ | Wurth | 865 060 440 001 |  | 1 | 10 | 0 | 10 | 50
C801, C802 | 22p | Capacitor_SMD:C_0402_1005Metric | ~ | Wurth | 885 012 005 009 |  | 2 | 20 | 100 | 0 | 0
C803, C806, C813 | 10u | Capacitor_SMD:C_0603_1608Metric | ~ | Wurth | 885 012 106 006 |  | 3 | 30 | 100 | 0 | 0
C805, C903 | 1u | Capacitor_SMD:C_0402_1005Metric | ~ | Wurth | 885 012 105 012 |  | 2 | 20 | 100 | 0 | 0
C904 | 1n | Capacitor_SMD:C_0402_1005Metric | ~ | Wurth | 885 012 205 044 |  | 1 | 10 | 100 | 0 | 0
D201, D301, D401 | Green LED | LED_SMD:LED_0603_1608Metric | ~ | Wurth | 150 060 GS5 504 0 |  | 3 | 30 | 0 | 30 | 100
D202, D203, D302, D303, D402, D403, D501-D503, D901, D1401-D1403 | Red LED | LED_SMD:LED_0603_1608Metric | ~ | Wurth | 150 060 RS5 504 0 |  | 13 | 130 | 0 | 130 | 300
D801-D804 | Blue LED | LED_SMD:LED_0603_1608Metric | ~ | Wurth | 150 060 BS5 504 0 |  | 4 | 40 | 0 | 40 | 100
D902, D903 | VS-15TQ060S-M3 | Package_TO_SOT_SMD:TO-263-2 | https://www.vishay.com/docs/94927/vs-15tq060s-m3.pdf | Farnell | VS-15TQ060S-M3 | 2909608 | 2 | 20 | 4 | 16 | 30
F501 | Fuse | Custom:0031.8201 | ~ | Wurth | 696 108 003 002 |  | 1 | 10 | 10 | 0 | 0
J101, J103 | Conn_02x19_Odd_Even | Connector_PinHeader_2.54mm:PinHeader_2x19_P2.54mm_Vertical | ~ | Farnell | SSW-119-01-T-D | 2667437 | 2 | 20 | 16 | 4 | 4
J102, J901 | Conn_01x02 | Custom:691311500102 | https://www.we-online.com/components/products/datasheet/691311500102.pdf | Wurth | 691 311 700 102 |  | 2 | 20 | 20 | 0 | 10
J104 | Conn_01x03 | Custom:691311500103 | https://www.we-online.com/components/products/datasheet/691311500103.pdf | Wurth | 691 311 700 103 |  | 1 | 10 | 0 | 10 | 20
J1101, J1102 | Conn_01x02 | Connector_JST:JST_XH_B2B-XH-A_1x02_P2.50mm_Vertical | ~ | Stock |  |  | 2 | 20 | 1000 | 0 | 0
J1301 | DE9_Receptacle_MountingHoles | Custom:618009233821 | https://www.we-online.com/components/products/datasheet/618009231421.pdf | Wurth | 618 009 231 421 |  | 1 | 10 | 19 | 0 | 0
J501 | PX0580-PC-12132 | Custom:PX0580-PC-12132 | PX0580-PC-12132 | RS | PX0580/PC/12132 | 261-5840 | 1 | 10 | 2 | 8 | 10
J801 | USB_C_Receptacle_USB2.0 | Connector_USB:USB_C_Receptacle_HRO_TYPE-C-31-M-12 | https://www.usb.org/sites/default/files/documents/usb_type-c.zip | Wurth | 629 722 000 214 |  | 1 | 10 | 19 | 0 | 0
J802 | Conn_01x05 | Connector_JST:JST_XH_B5B-XH-A_1x05_P2.50mm_Vertical | ~ | Stock |  |  | 1 | 10 | 1000 | 0 | 0
J803 | Conn_ST_STDC14 | Connector_PinHeader_1.27mm:PinHeader_2x07_P1.27mm_Vertical_SMD | https://www.st.com/content/ccc/resource/technical/document/user_manual/group1/99/49/91/b6/b2/3a/46/e5/DM00526767/files/DM00526767.pdf/jcr:content/translations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 | Stock |  |  | 1 | 10 | 10 | 0 | 0
J804 | Conn_01x04 | Connector_JST:JST_XH_B4B-XH-A_1x04_P2.50mm_Vertical | ~ | Stock |  |  | 1 | 10 | 1000 | 0 | 0
L801 | 39n | Inductor_SMD:L_0603_1608Metric | ~ | Wurth | 744 786 013 9 |  | 1 | 10 | 0 | 10 | 100
Q1101 | SQ2310ES | Package_TO_SOT_SMD:SOT-23 | ~ | RS | SQ2310ES-T1_BE3 | 787-9443 | 1 | 10 | 9 | 1 | 20
Q201, Q301, Q401 | HCPL-315J-500E | Custom:SO-16_HCPL-315J_BRA | HCPL-315J-500E | RS | HCPL-315J-500E | 174-4163 | 3 | 30 | 17 | 13 | 20
Q202, Q203, Q302, Q303, Q402, Q403 | IRF540N | Package_TO_SOT_THT:TO-220-3_Vertical | http://www.irf.com/product-info/datasheets/data/irf540n.pdf | RS | IRF540NPBF | 914-8154 | 6 | 60 | 13 | 47 | 100
Q901 | BUK9637-100E | Package_TO_SOT_SMD:TO-263-2 |  | Farnell | BUK9637-100E,118 | 2254193 | 1 | 10 | 2 | 8 | 10
R1101 | 22 | Resistor_SMD:R_0402_1005Metric | ~ | Stock |  |  | 1 | 10 | 200 | 0 | 0
R1201 | 200 | Resistor_SMD:R_0402_1005Metric | ~ | Stock |  |  | 1 | 10 | 200 | 0 | 0
R201, R202, R301, R302, R401, R402 | 170 | Resistor_SMD:R_0402_1005Metric | ~ | Stock |  |  | 6 | 60 | 200 | 0 | 0
R203-R205, R303-R305, R403-R405, R503, R804-R807, R901 | 390 | Resistor_SMD:R_0402_1005Metric | ~ | Farnell | CRCW0402390RFKEDC | 4177482 | 15 | 150 | 0 | 150 | 5000
R206, R208, R306, R308, R406, R408 | 30 | Resistor_SMD:R_1206_3216Metric | ~ | Stock |  |  | 6 | 60 | 200 | 0 | 0
R207, R209, R307, R309, R407, R409, R801, R902, R1102, R1401-R1403 | 10k | Resistor_SMD:R_0402_1005Metric | ~ | Farnell | MC00625W0402110K | 2130433 | 12 | 120 | 0 | 120 | 10000
R210, R310, R410, R601 | 160k | Resistor_SMD:R_0402_1005Metric | ~ | Stock |  |  | 4 | 40 | 200 | 0 | 0
R211, R311, R411, R602 | 1k | Resistor_SMD:R_0402_1005Metric | ~ | Farnell | MCWR04X1001FTL | 2446437 | 4 | 40 | 0 | 40 | 10000
R501 | 2k7 | Resistor_SMD:R_0402_1005Metric | ~ | Stock |  |  | 1 | 10 | 200 | 0 | 0
R502 | 680 | Resistor_SMD:R_0402_1005Metric | ~ | Stock |  |  | 1 | 10 | 200 | 0 | 0
R701 | 27k | Resistor_SMD:R_0402_1005Metric | ~ | Stock |  |  | 1 | 10 | 200 | 0 | 0
R802, R803 | 5.1k | Resistor_SMD:R_0402_1005Metric | ~ | Stock |  |  | 2 | 20 | 200 | 0 | 0
R903 | 4.7 | Resistor_SMD:R_1206_3216Metric | ~ | Stock |  |  | 1 | 10 | 200 | 0 | 0
SW801-SW805 | SW_Push | Custom:435451019820 | ~ | Wurth | 435 451 019 820 |  | 5 | 50 | 15 | 35 | 100
U1201 | TCN75A | Package_SO:SOIC-8_3.9x4.9mm_P1.27mm | https://docs.rs-online.com/fc92/0900766b80d0dfb5.pdf | RS | TCN75AVOA | 738-6014 | 1 | 10 | 4 | 6 | 10
U1301 | MAX3097ECSE+ | Package_SO:SOIC-16_3.9x9.9mm_P1.27mm | https://www.mouser.fr/datasheet/2/609/MAX3097E_MAX3098E-3128450.pdf | Farnell | MAX3097ECSE+ | 2518786 | 1 | 10 | 0 | 10 | 15
U201, U202, U301, U302, U401, U402 | MPRB2415S-6W | Custom:MPRB2415S |  | Mouser | PQQ6W-Q24-S15-S | 490-PQQ6W-Q24-S15-S | 6 | 60 | 11 | 49 | 60
U203, U303, U403, U602 | HCPL-7800-500E | Custom:DIP-8 Gull Wing |  | RS | HCPL-7800A-500E | 174-4179 | 4 | 40 | 8 | 32 | 40
U204, U304, U404, U601 | GO 10-SME/SP3 | Custom:SOIC8-GO-SME&slash_SP3_LEM | GO 10-SME | Farnell | GO 10-SME/SP3 | 3796461 | 4 | 40 | 9 | 31 | 40
U501 | MP-LD30-23B12R2 | Custom:MP-LD30-23B15R2 | MP-LD30-23B12R2 | Farnell | MP-LD30-23B15R2 | 3780527 | 1 | 10 | 2 | 8 | 10
U502 | 173010542 | Custom:173010578 | 173010542 | Wurth | 173 010 542 |  | 1 | 10 | 19 | 0 | 0
U503 | AZ1117-3.3 | Package_TO_SOT_SMD:SOT-223-3_TabPin2 | https://www.diodes.com/assets/Datasheets/AZ1117.pdf | RS | AZ1117H-3.3TRE1 | 921-0701 | 1 | 10 | 49 | 0 | 0
U701 | 17791063215 | Custom:17791063215 | https://www.we-online.com/components/products/datasheet/17791063215.pdf | Wurth | 177 910 632 15 |  | 1 | 10 | 19 | 0 | 0
U801 | STM32G474RETx | Package_QFP:LQFP-64_10x10mm_P0.5mm | https://www.st.com/resource/en/datasheet/stm32g474re.pdf | RS | STM32G474RET6 | 193-9861 | 1 | 10 | 2 | 8 | 10
U802 | USBLC6-2SC6 | Package_TO_SOT_SMD:SOT-23-6 | https://www.st.com/resource/en/datasheet/usblc6-2.pdf | RS | USBLC6-2SC6 | 624-7693 | 1 | 10 | 9 | 1 | 10
U901 | ACPL-077L | Package_SO:SO-8_3.9x4.9mm_P1.27mm |  | RS | ACPL-077L-500E | 230-5293 | 1 | 10 | 3 | 7 | 10
U902 | TC1412 | Package_SO:SOIC-8_3.9x4.9mm_P1.27mm |  | RS | TC1412NEOA | 1834898 | 1 | 10 | 2 | 8 | 10
Y801 | 16M | Custom:ABLS-7.3728MHZ-CL-RESR-A-1-G-F | https://4donline.ihs.com/images/VipMasterIC/IC/ABRC/ABRCS03441/ABRCS03441-1.pdf?hkey=6D3A4C79FDBF58556ACFDE234799DDF0 | Farnell | ABLS-16.000MHZ-20-B-3-H-T | 3228387 | 1 | 10 | 48 | 0 | 0
Accessories
Reference | Value | Footprint | Datasheet | Fournisseur | MFR | Ref | Qty | Total | Stock | Diff | Commande
 | Clip Cover |  |  | Wurth | 696 122 003 001 |  | 1 | 10 | 0 | 10 | 20
 | Résistance à montage sur châssis Bobinée, 4.7Ω 100W ±5% |  |  | RS | HSC1004R7J | 720-5407 | 1 | 10 | 3 | 7 | 10
 | Crème à braser 653555 Loctite MP218, 500g Bac |  |  | RS | 653555 | 506-4289 | 0.1 | 1 | 0 | 1 | 1
 | Flux de soudure RS PRO, Stylo de 12ml |  |  | RS |  | 251-3637 | 0.4 | 4 |  | 4 | 5
 | Cartouche fusible RS PRO, 500mA 5 x 20mm Type F 250V c.a. |  |  | RS |  | 563-463 | 10 | 100 |  | 100
 | Radiateur |  |  | Farnell | 205AB1500B | 523173 | 1 | 10 | 0 | 10 | 10
 | Crème à braser 653555 Loctite MP218, 500g Bac |  |  | RS | 653555 | 506-4289 | 1 | 1 | 0 | 1 | 1
 | Kit isolant thermique, TO-220, Caoutchouc silicone, 1,6W/m.K, 6kV, 0,23 mm, 10 ohm-cm |  |  | Farnell | MK3306/TG | 522636 | 6 | 60 | 0 | 60 | 100
 | AXIAL FAN, 40MM, 5VDC, 7.1CFM, 23DBA |  |  | Farnell | MC011490 | 3217981 | 2 | 20 | 0 | 20 | 20
 | Vis à six pans creux, M3 x 6mm, en Acier |  |  | RS |  | 467-9773 | 1 | 1 | 0 | 1 | 1
 | Vis 6 pans à tête bombée hexagonale, M3 x 8mm, en Acier |  |  | RS |  | 281-186 | 1 | 1 | 0 | 1 | 1
 | Rondelle, Nylon, M3, Plat, Interne 3,2mm, Externe 7mm |  |  | Farnell | MP008055 | 3804766 | 1 | 1 | 0 | 1 | 1
ESE/EVE
Reference | Value | Footprint | Datasheet | Fournisseur | MFR | Ref | Qty | Total | Stock | Diff | Commande
 | Carte microcontrôleur IoT, FireBeetle, ESP32, cartes de développement Arduino |  |  | Farnell | DFR0478 | 3517881 |  |  |  |  | 10
 | WS-MITV THT Terminal with Lever Micro Switch, 12.8 x 5.8 mm |  |  | Wurth |  | 463 092 370 402 |  |  |  |  | 100
 | WS-TOTV Ø 6.35mm Panel Cut-Out Vertical Operation Toggle Switch NEW |  |  | Wurth |  | 472 123 010 111 |  |  |  |  | 20
 | MagI³C-FDSM Fixed Step Down Regulator Module 5V 1A |  |  | Wurth |  | 173 010 542 |  |  |  |  | 50

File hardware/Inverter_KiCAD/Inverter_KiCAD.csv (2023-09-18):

Source: | /home/nicolas/git/AAP_ENSEA_Inverter/Inverter_KiCAD/Inverter_KiCAD.kicad_sch
Date: | lun. 18 sept. 2023 08:32:15
Tool: | Eeschema 7.0.7-7.0.7~ubuntu22.04.1
Generator: | /usr/share/kicad/plugins/bom_csv_grouped_by_value.py
Component Count: | 220
Collated Components:
Item | Qty | Reference(s) | Value | LibPart | Footprint | Datasheet | DNP | Fournisseur | MFR | Ref | URL | Vmax
1 | 6 | C201, C202, C301, C302, C401, C402 | 100u | Device:C_Polarized | Capacitor_SMD:CP_Elec_6.3x7.7 | ~ |  | Wurth | 865 060 445 005 |  |  | 25V
2 | 7 | C203, C204, C303, C304, C403, C404, C502 | 22u | Device:C_Polarized | Capacitor_SMD:CP_Elec_5x5.4 | ~ |  | Wurth | 865 060 442 002 |  |  | 25V
3 | 4 | C205, C305, C405, C604 | 10n | Device:C_Small | Capacitor_SMD:C_0402_1005Metric | ~ |  | Wurth | 885 012 205 050
4 | 3 | C206, C306, C406 | 10u | Device:C_Small | Capacitor_SMD:C_2220_5650Metric | https://www.we-online.com/components/products/datasheet/885012214001.pdf |  | Wurth | 885 012 214 001 |  | https://www.we-online.com/components/products/datasheet/885012214001.pdf
5 | 24 | C207, C208, C307, C308, C407, C408, C605, C606, C804, C807, C808, C809, C810, C811, C812, C814, C815, C816, C817, C818, C901, C902, C1201, C1301 | 100n | Device:C_Small | Capacitor_SMD:C_0402_1005Metric | ~ |  | Wurth | 885 012 105 018
6 | 12 | C209, C210, C211, C309, C310, C311, C409, C410, C411, C601, C602, C603 | 4.7n | Device:C_Small | Capacitor_SMD:C_0402_1005Metric | ~ |  | Wurth | 885 012 205 048
7 | 1 | C501 | 10u | Device:C_Polarized | Capacitor_SMD:CP_Elec_4x5.4 | ~ |  | Wurth | 865 060 440 001
8 | 2 | C801, C802 | 22p | Device:C_Small | Capacitor_SMD:C_0402_1005Metric | ~ |  | Wurth | 885 012 005 009
9 | 3 | C803, C806, C813 | 10u | Device:C_Small | Capacitor_SMD:C_0603_1608Metric | ~ |  | Wurth | 885 012 106 006
10 | 2 | C805, C903 | 1u | Device:C_Small | Capacitor_SMD:C_0402_1005Metric | ~ |  | Wurth | 885 012 105 012
11 | 1 | C904 | 1n | Device:C_Small | Capacitor_SMD:C_0402_1005Metric | ~ |  | Wurth | 885 012 205 044
12 | 5 | C1001, C1002, C1003, C1004, C1005 | 1.5m | Device:C_Polarized | Capacitor_THT:CP_Radial_D35.0mm_P10.00mm_SnapIn | ~ |  | Wurth | 861 011 086 027
13 | 3 | D201, D301, D401 | Green LED | Device:LED | LED_SMD:LED_0603_1608Metric | ~ |  | Wurth | 150 060 GS5 504 0
14 | 12 | D202, D203, D302, D303, D402, D403, D501, D502, D503, D1401, D1402, D1403 | Red LED | Device:LED | LED_SMD:LED_0603_1608Metric | ~ |  | Wurth | 150 060 RS5 504 0
15 | 4 | D801, D802, D803, D804 | Blue LED | Device:LED | LED_SMD:LED_0603_1608Metric | ~ |  | Wurth | 150 060 BS5 504 0
16 | 1 | D901 | Red LED | Device:LED_Small | LED_SMD:LED_0603_1608Metric | ~ |  | Wurth | 150 060 RS5 504 0
17 | 2 | D902, D903 | VS-15TQ060S-M3 | Device:D_Schottky | Package_TO_SOT_SMD:TO-263-2 | https://www.vishay.com/docs/94927/vs-15tq060s-m3.pdf |  | Farnell | VS-15TQ060S-M3 | 2909608
18 | 1 | F501 | Fuse | Device:Fuse | Custom:0031.8201 | ~ |  | Wurth | 696 108 003 002
19 | 14 | H101, H102, H103, H104, H105, H106, H107, H108, H109, H110, H111, H112, H113, H114 | MountingHole_Pad | Mechanical:MountingHole_Pad | MountingHole:MountingHole_3.2mm_M3_Pad_Via | ~ |  |  | -
20 | 2 | J101, J103 | Conn_02x19_Odd_Even | Connector_Generic:Conn_02x19_Odd_Even | Connector_PinHeader_2.54mm:PinHeader_2x19_P2.54mm_Vertical | ~ |  | Farnell | SSW-119-01-T-D | 2667437
21 | 2 | J102, J901 | Conn_01x02 | Connector_Generic:Conn_01x02 | Custom:691311500102 | https://www.we-online.com/components/products/datasheet/691311500102.pdf |  | Wurth | 691 311 700 102
22 | 1 | J104 | Conn_01x03 | Connector_Generic:Conn_01x03 | Custom:691311500103 | https://www.we-online.com/components/products/datasheet/691311500103.pdf |  | Wurth | 691 311 700 103
23 | 1 | J501 | PX0580-PC-12132 | PX0580-PC-12132:PX0580-PC-12132 | Custom:PX0580-PC-12132 | PX0580-PC-12132 |  | RS | PX0580/PC/12132 | 261-5840
24 | 1 | J801 | USB_C_Receptacle_USB2.0 | Connector:USB_C_Receptacle_USB2.0 | Connector_USB:USB_C_Receptacle_HRO_TYPE-C-31-M-12 | https://www.usb.org/sites/default/files/documents/usb_type-c.zip |  | Wurth | 629 722 000 214
25 | 1 | J802 | Conn_01x05 | Connector_Generic:Conn_01x05 | Connector_JST:JST_XH_B5B-XH-A_1x05_P2.50mm_Vertical | ~ |  | Stock
26 | 1 | J803 | Conn_ST_STDC14 | Connector:Conn_ST_STDC14 | Connector_PinHeader_1.27mm:PinHeader_2x07_P1.27mm_Vertical_SMD | https://www.st.com/content/ccc/resource/technical/document/user_manual/group1/99/49/91/b6/b2/3a/46/e5/DM00526767/files/DM00526767.pdf/jcr:content/translations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 |  | Stock
27 | 1 | J804 | Conn_01x04 | Connector_Generic:Conn_01x04 | Connector_JST:JST_XH_B4B-XH-A_1x04_P2.50mm_Vertical | ~ |  | Stock
28 | 2 | J1101, J1102 | Conn_01x02 | Connector_Generic:Conn_01x02 | Connector_JST:JST_XH_B2B-XH-A_1x02_P2.50mm_Vertical | ~ |  | Stock
29 | 1 | J1301 | DE9_Receptacle_MountingHoles | Connector:DE9_Receptacle_MountingHoles | Custom:618009233821 | https://www.we-online.com/components/products/datasheet/618009231421.pdf |  | Wurth | 618 009 231 421
30 | 1 | L801 | 39n | Device:L_Small | Inductor_SMD:L_0603_1608Metric | ~ |  | Wurth | 744 786 013 9
31 | 3 | Q201, Q301, Q401 | HCPL-315J-500E | Custom:HCPL-315J-500E | Custom:SO-16_HCPL-315J_BRA | HCPL-315J-500E |  | RS | HCPL-315J-500E | 174-4163
32 | 6 | Q202, Q203, Q302, Q303, Q402, Q403 | IRF540N | Transistor_FET:IRF540N | Package_TO_SOT_THT:TO-220-3_Vertical | http://www.irf.com/product-info/datasheets/data/irf540n.pdf |  | RS | IRF540NPBF | 914-8154
33 | 1 | Q901 | BUK9637-100E | Transistor_FET:IRFS4229 | Package_TO_SOT_SMD:TO-263-2 | https://www.infineon.com/dgdl/irfs4229pbf.pdf?fileId=5546d462533600a401535639fdc421a1 |  | Farnell | BUK9637-100E,118 | 2254193
34 | 1 | Q1101 | SQ2310ES | Device:Q_NMOS_GSD | Package_TO_SOT_SMD:SOT-23 | ~ |  | RS | SQ2310ES-T1_BE3 | 787-9443
35 | 6 | R201, R202, R301, R302, R401, R402 | 170 | Device:R_Small | Resistor_SMD:R_0402_1005Metric | ~ |  | Stock
36 | 15 | R203, R204, R205, R303, R304, R305, R403, R404, R405, R503, R804, R805, R806, R807, R901 | 390 | Device:R_Small | Resistor_SMD:R_0402_1005Metric | ~ |  | Farnell | CRCW0402390RFKEDC | 4177482
37 | 6 | R206, R208, R306, R308, R406, R408 | 30 | Device:R_Small | Resistor_SMD:R_1206_3216Metric | ~ |  | Stock
38 | 14 | R207, R209, R307, R309, R407, R409, R801, R808, R809, R810, R902, R1401, R1402, R1403 | 10k | Device:R_Small | Resistor_SMD:R_0402_1005Metric | ~ |  | Farnell | MC00625W0402110K | 2130433
39 | 4 | R210, R310, R410, R601 | 160k | Device:R_Small | Resistor_SMD:R_0402_1005Metric | ~ |  | Stock
40 | 4 | R211, R311, R411, R602 | 1k | Device:R_Small | Resistor_SMD:R_0402_1005Metric | ~ |  | Farnell | MCWR04X1001FTL | 2446437
41 | 1 | R501 | 2k7 | Device:R_Small | Resistor_SMD:R_0402_1005Metric | ~ |  | Stock
42 | 1 | R502 | 680 | Device:R_Small | Resistor_SMD:R_0402_1005Metric | ~ |  | Stock
43 | 1 | R701 | 27k | Device:R_Small | Resistor_SMD:R_0402_1005Metric | ~ |  | Stock
44 | 2 | R802, R803 | 5.1k | Device:R_Small | Resistor_SMD:R_0402_1005Metric | ~ |  | Sotck
45 | 1 | R903 | 4.7 | Device:R_Small | Resistor_SMD:R_1206_3216Metric | ~ |  | Stock
46 | 1 | R1101 | 22 | Device:R_Small | Resistor_SMD:R_0402_1005Metric | ~ |  | Stock
47 | 1 | R1102 | 10k | Device:R_Small_US | Resistor_SMD:R_0402_1005Metric | ~ |  | Farnell | MC00625W0402110K | 2130433
48 | 1 | R1201 | 200 | Device:R_Small | Resistor_SMD:R_0402_1005Metric | ~ |  | Stock
49 | 5 | SW801, SW802, SW803, SW804, SW805 | SW_Push | Switch:SW_Push | Custom:435451019820 | ~ |  | Wurth | 435 451 019 820
50 | 3 | U201, U301, U401 | MPRB2415S-6W | Custom:MPRB2415S-6W | Custom:MPRB2415S |  |  | Farnell* | MPRB2415S/PQQ6W-Q24-D15-S | 3652723/4138610
51 | 3 | U202, U302, U402 | MPRB2415S-6W | :MPRB2415S-6W_1 | Custom:MPRB2415S |  |  | Farnell* | MPRB2415S/PQQ6W-Q24-D15-S | 3652723/4138610
52 | 4 | U203, U303, U403, U602 | HCPL-7800-500E | Custom:HCPL-7800-500E | Custom:DIP-8 Gull Wing |  |  | RS | HCPL-7800A-500E | 174-4179
53 | 4 | U204, U304, U404, U601 | GO 10-SME/SP3 | Custom:GO_10-SME | Custom:SOIC8-GO-SME&slash_SP3_LEM | GO 10-SME |  | Farnell | GO 10-SME/SP3 | 3796461
54 | 1 | U501 | MP-LD30-23B12R2 | MP-LD30-23B15R2:MP-LD30-23B12R2 | Custom:MP-LD30-23B15R2 | MP-LD30-23B12R2 |  | Farnell | MP-LD30-23B15R2 | 3780527
55 | 1 | U502 | 173010542 | Custom:173010542 | Custom:173010578 | 173010542 |  | Wurth | 173 010 542
56 | 1 | U503 | AZ1117-3.3 | Regulator_Linear:AZ1117-3.3 | Package_TO_SOT_SMD:SOT-223-3_TabPin2 | https://www.diodes.com/assets/Datasheets/AZ1117.pdf |  | RS | AZ1117H-3.3TRE1 | 921-0701
57 | 1 | U701 | 17791063215 | Custom:17791063215 | Custom:17791063215 | https://www.we-online.com/components/products/datasheet/17791063215.pdf |  | Wurth | 177 910 632 15
58 | 1 | U801 | STM32G474RETx | MCU_ST_STM32G4:STM32G474RETx | Package_QFP:LQFP-64_10x10mm_P0.5mm | https://www.st.com/resource/en/datasheet/stm32g474re.pdf |  | RS | STM32G474RET6 | 193-9861
59 | 1 | U802 | USBLC6-2SC6 | Power_Protection:USBLC6-2SC6 | Package_TO_SOT_SMD:SOT-23-6 | https://www.st.com/resource/en/datasheet/usblc6-2.pdf |  | RS | USBLC6-2SC6 | 624-7693
60 | 1 | U901 | ACPL-077L | Custom:ACPL-077L | Package_SO:SO-8_3.9x4.9mm_P1.27mm |  |  | RS | ACPL-077L-500E | 230-5293
61 | 1 | U902 | TC1412 | Custom:TC1412 | Package_SO:SOIC-8_3.9x4.9mm_P1.27mm |  |  | RS | TC1412NEOA | 1834898
62 | 1 | U1201 | TCN75A | Custom:TCN75A | Package_SO:SOIC-8_3.9x4.9mm_P1.27mm | https://docs.rs-online.com/fc92/0900766b80d0dfb5.pdf |  | RS | TCN75AVOA | 738-6014
63 | 1 | U1301 | MAX3097ECSE+ | Custom:MAX3097ECSE+ | Package_SO:SOIC-16_3.9x9.9mm_P1.27mm | https://www.mouser.fr/datasheet/2/609/MAX3097E_MAX3098E-3128450.pdf |  | Farnell | MAX3097ECSE+ | 2518786
64 | 1 | Y801 | 16M | Device:Crystal | Custom:ABLS-7.3728MHZ-CL-RESR-A-1-G-F | https://4donline.ihs.com/images/VipMasterIC/IC/ABRC/ABRCS03441/ABRCS03441-1.pdf?hkey=6D3A4C79FDBF58556ACFDE234799DDF0 |  | Farnell | ABLS-16.000MHZ-20-B-3-H-T | 3228387

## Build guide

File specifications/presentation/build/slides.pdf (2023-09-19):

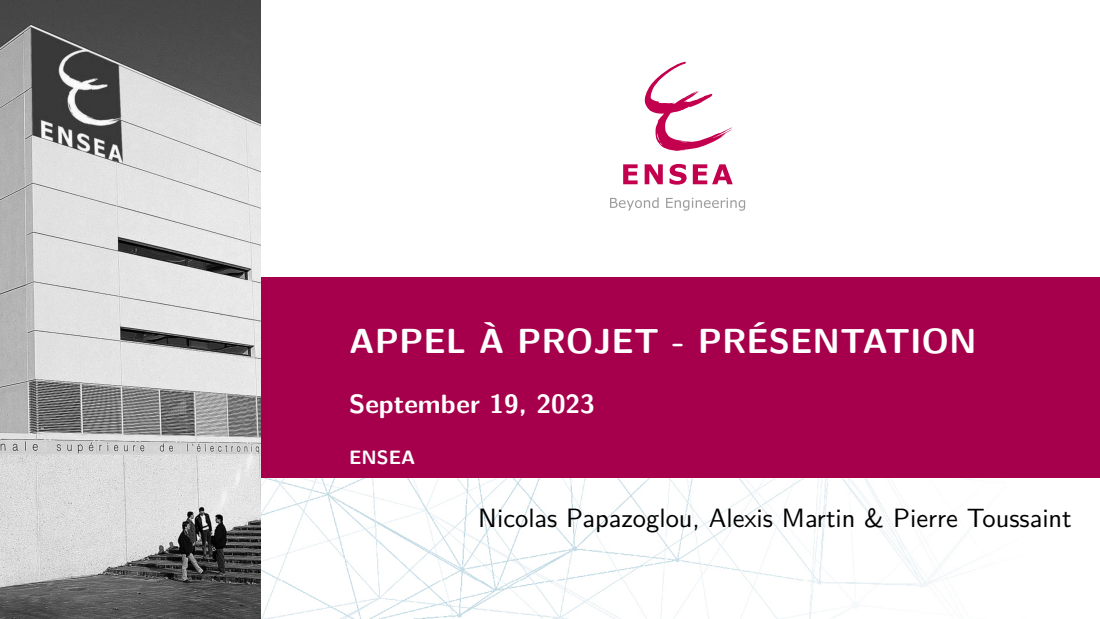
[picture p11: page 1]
September 19, 2023; ENSEA

APPEL À PROJET - PRÉSENTATION

Nicolas Papazoglou, Alexis Martin & Pierre Toussaint

## Rappel

Porteurs du projet : Nicolas Papazoglou, Alexis Martin, Pierre Toussaint,
Demande budgétaire : 64 HETD, Budget (DEE) : 400-500e/maquette,

Activités concernées : enseignements d’électrotechnique et d’automatique.

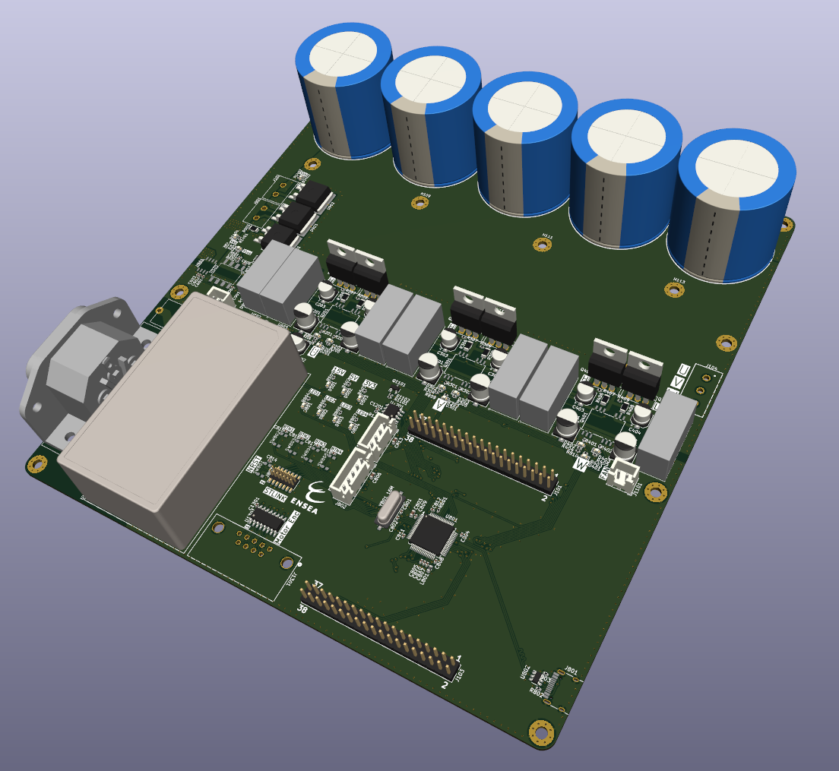
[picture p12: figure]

Lien github (https://github.com/DBXYD/AAP_ENSEA_Inverter)

N.P. - A.M. - P.T. 2 / 8

## Contexte

Maquette de TP : onduleur triphasé,
TP en 3eme année (Enseignements d’électrotechnique et d’automatique) : ESE_3745 Actionneur et automatique appliquée
MSC_3805 Systèmes d’Acquision et de commande
12 maquettes obsolète Powermodule MC1L 3-Phase (Microchip) : Pannes récurentes :
Perte de temps pour les étudiants,
Recherche de panne et réparation par les professeurs,
Boite noire pour les étudiants.

## Objectif : Réalisation maquette pédagogique

Objectifs :
1 | Une maquette fiable pour les TPs d’électrotechnique et automatique → Gain en temps et en autonomie pour les étudiants,
2 | Feedback automatique en fonction des erreurs détectées, → Gain en autonomie pour les étudiants, possibilité de travail hors séance sans supervision d’un professeur,
3 | Projet open-source (disponible sur github), (https://github.com/DBXYD/AAP_ENSEA_Inverter)
4 | Compréhension globale possible par les étudiants, application de l’ensemble de leurs cours dans une maquette,
5 | Création modulaire, réutilisable dans d’autres cours/projets,
6 | Evolution possible à d’autres enseignements (buck/boost, 4Q, brushless, moteurs synchrones, asservissement, etc...),
7 | Maintenance facile et rapide.

## Bilan

1 | Cahier des charges | ,
2 | Schéma d’architecture | ,
3 | Choix des composants | ,
4 | Prototypage et tests unitaires électriques | ,
5 | Réalisation software et tests complets (50%),
6 | Réalisation mécanique (boitier) (50%),
7 | Documentation (github). (https://github.com/DBXYD/AAP_ENSEA_Inverter) (80%)

## Bilan

1 | Cahier des charges | ,
2 | Schéma d’architecture | ,
3 | Choix des composants | ,
4 | Prototypage et tests unitaires électriques | ,
5 | Réalisation software et tests complets (50%),
6 | Réalisation mécanique (boitier) (50%),
7 | Documentation (github). (https://github.com/DBXYD/AAP_ENSEA_Inverter) (80%)

Remarque :
Coût : 300e/maquette,

8 cartes en fabrication dans l’immédiat

Beaucoup de composants gratuits

## Schematic

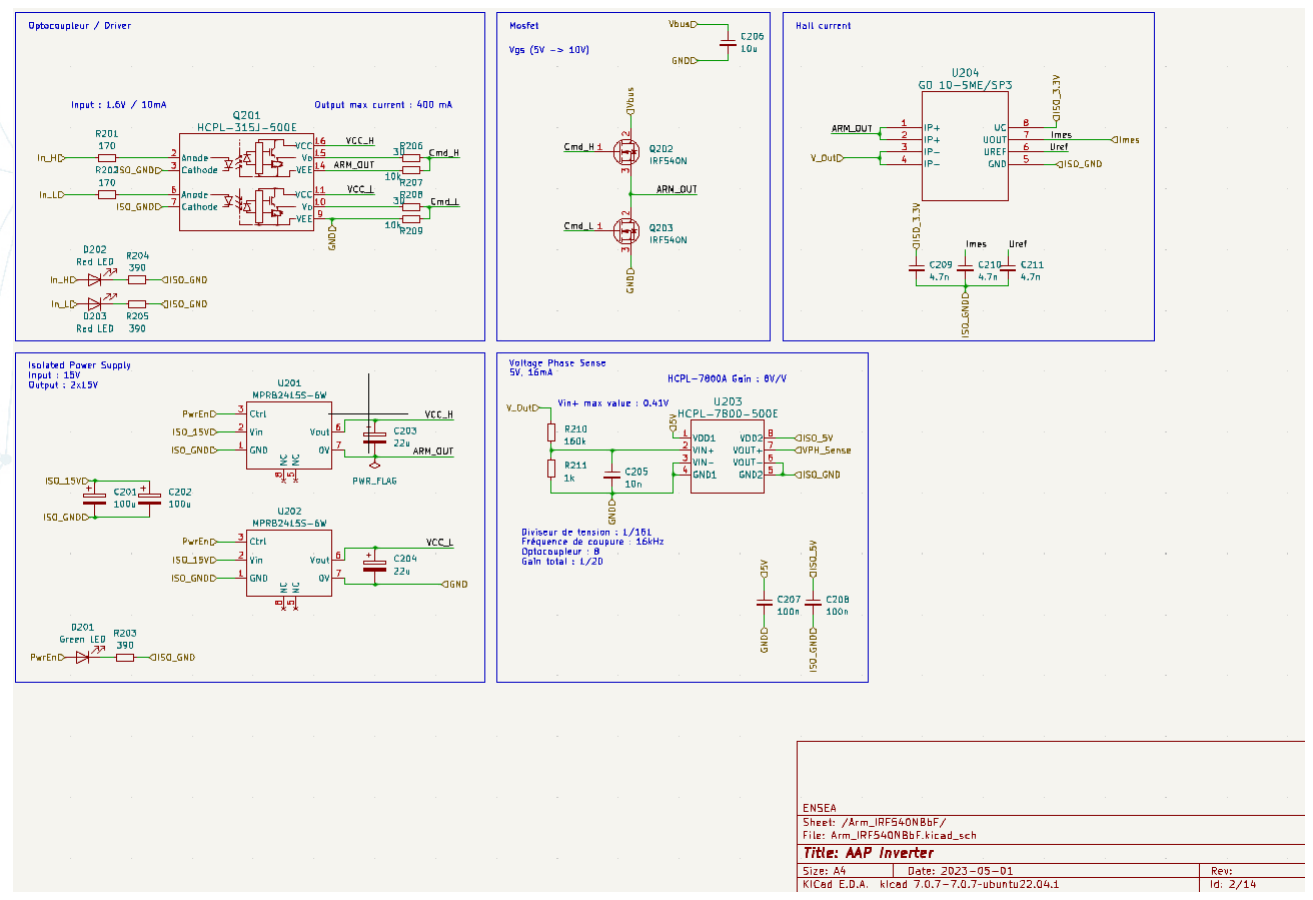
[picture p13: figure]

## PCB

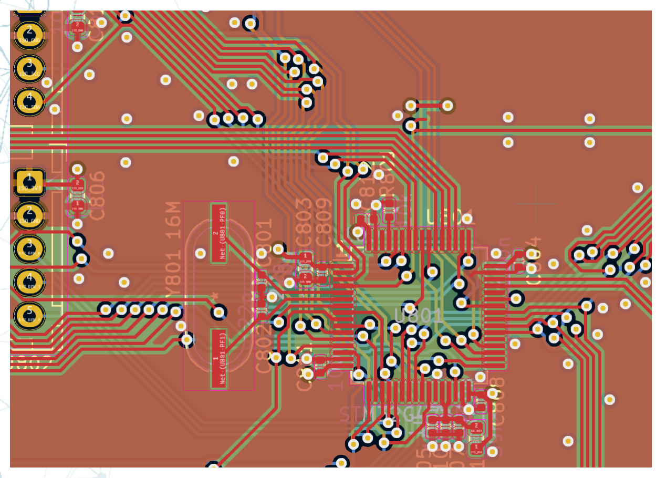
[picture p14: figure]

242 composants (60 différents),

2000 segments de pistes,
906 pads
225 signaux

## La suite

Idée 1 :
Connexion usb fonctionnelle

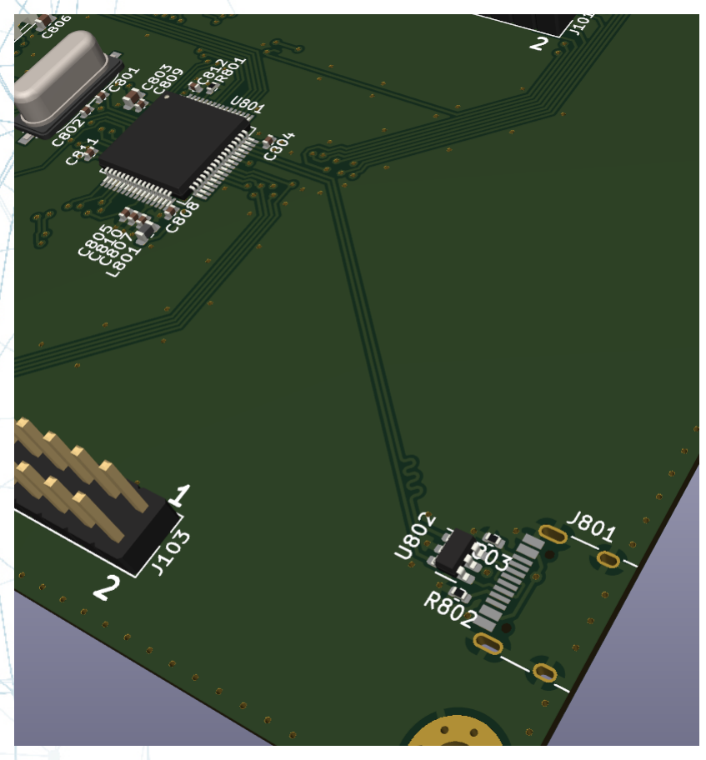
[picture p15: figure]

Possibilité de récupérer toutes les données internes
Programme et interface (Python) pour afficher de façon didactique l’état du moteur

Idée 2 :
Possibilité de TP de puissance à distance Idée 3 :
Portage de ce projet sur d’autres cours Carte fille différente (remplacement de la Nucléo)

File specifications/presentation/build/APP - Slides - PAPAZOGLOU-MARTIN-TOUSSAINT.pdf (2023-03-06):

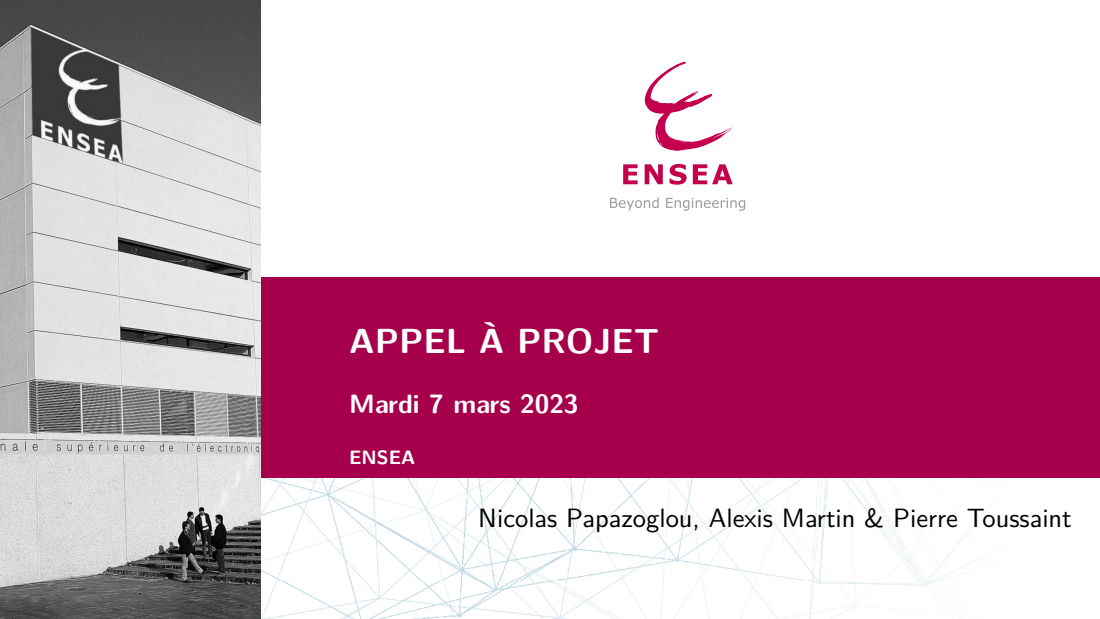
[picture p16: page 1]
APPEL À PROJET; Mardi 7 mars 2023; ENSEA

Nicolas Papazoglou, Alexis Martin & Pierre Toussaint

## Appel à projet

Porteurs du projet : Alexis Martin, Nicolas Papazoglou, Pierre Toussaint, Demande budgétaire : 64 HETD, Budget (DEE) : 400-500e/maquette,

Activités concernées : enseignements d’électrotechnique et d’automatique.


Lien github (https://github.com/DBXYD/AAP_ENSEA_Inverter)

N.P. - A.M. - P.T. 2 / 8

## Contexte

Maquette de TP : onduleur triphasé,
TP en 3eme année (Enseignements d’électrotechnique et d’automatique) : AEI_3121 Commande numérique directe de dispositifs
ESE_3745 Actionneur et automatique appliquée
MSC_3805 Systèmes d’Acquision et de commande
12 maquettes obsolète Powermodule MC1L 3-Phase (Microchip) : Pannes récurentes :
Perte de temps pour les étudiants,
Recherche de panne et réparation par les professeurs,
Boite noire pour les étudiants.

## Objectif : Réalisation maquette pédagogique

Objectifs :
1 | Une maquette fiable pour les TPs d’électrotechnique et automatique → Gain en temps et en autonomie pour les étudiants,
2 | Feedback automatique en fonction des erreurs détectées, → Gain en autonomie pour les étudiants, possibilité de travail hors séance sans supervision d’un professeur,
3 | Projet open-source (disponible sur github), (https://github.com/DBXYD/AAP_ENSEA_Inverter)
4 | Compréhension globale possible par les étudiants, application de l’ensemble de leurs cours dans une maquette,
5 | Création modulaire, réutilisable dans d’autres cours/projets,
6 | Evolution possible à d’autres enseignements (buck/boost, 4Q, brushless, moteurs synchrones, asservissement, etc...),
7 | Maintenance facile et rapide.

## Travail à effectuer

1 | Cahier des charges (déjà effectué),
2 | Schéma d’architecture (déjà effectué),
3 | Choix des composants (disponibles et actuels pour une maintenibilité la plus longue possible),
4 | Prototypage et tests unitaires électriques,
5 | Réalisation software et tests complets,
6 | Réalisation mécanique (boitier),
7 | Intégration complète,
8 | Documentation (github). (https://github.com/DBXYD/AAP_ENSEA_Inverter)

## Travail déjà effectué : Cahier des charges

Onduleur triphasé 60V / 15A,
Protections surtensions et surintensités,
Commande de mise sous tension,
Commande UART,
Utilisable en commande “brushless” : entrées position “hall” , Utilisable en commande vectorielle ou MCC : entrée position “encoder”, Protection alimentation non réversible : module “freinage”, Vérification des temps morts,
Mesure de courants (hall) dans les 3 phases + entrée,
Mesure de tension dans les 3 phases + entrée, Alimentation externe secteur,
Affichage erreurs, intensité PWM (affiche externe), Sorties mesures de courants et PWMs,
Boitier,
Tenue thermique,
Isolation galvanique. | N.P. - A.M. - P.T. 6 / 8

## Travail déjà effectué : Schéma d’architecture

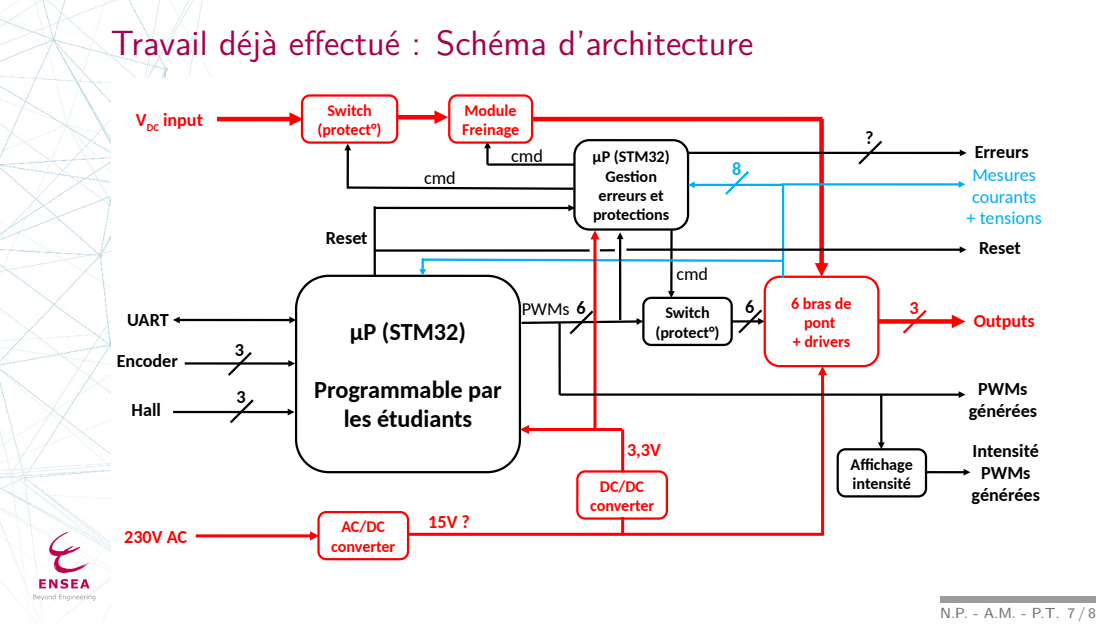
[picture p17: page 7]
µP (STM32); Gestion; erreurs et; protections; Programmable par; les étudiants; Switch; (protect°); 6 bras de; pont; + drivers; Outputs; VDC input; UART; cmd; converter; Encoder; Hall; Module; Freinage; PWMs; Erreurs; Mesures; courants; + tensions; Reset; générées; Affichage; intensité; Intensité

## Dead-line et rémunération

Prototype fonctionnel pour la rentrée de septembre 2023,

Rémunération demandée : 64 HETD.

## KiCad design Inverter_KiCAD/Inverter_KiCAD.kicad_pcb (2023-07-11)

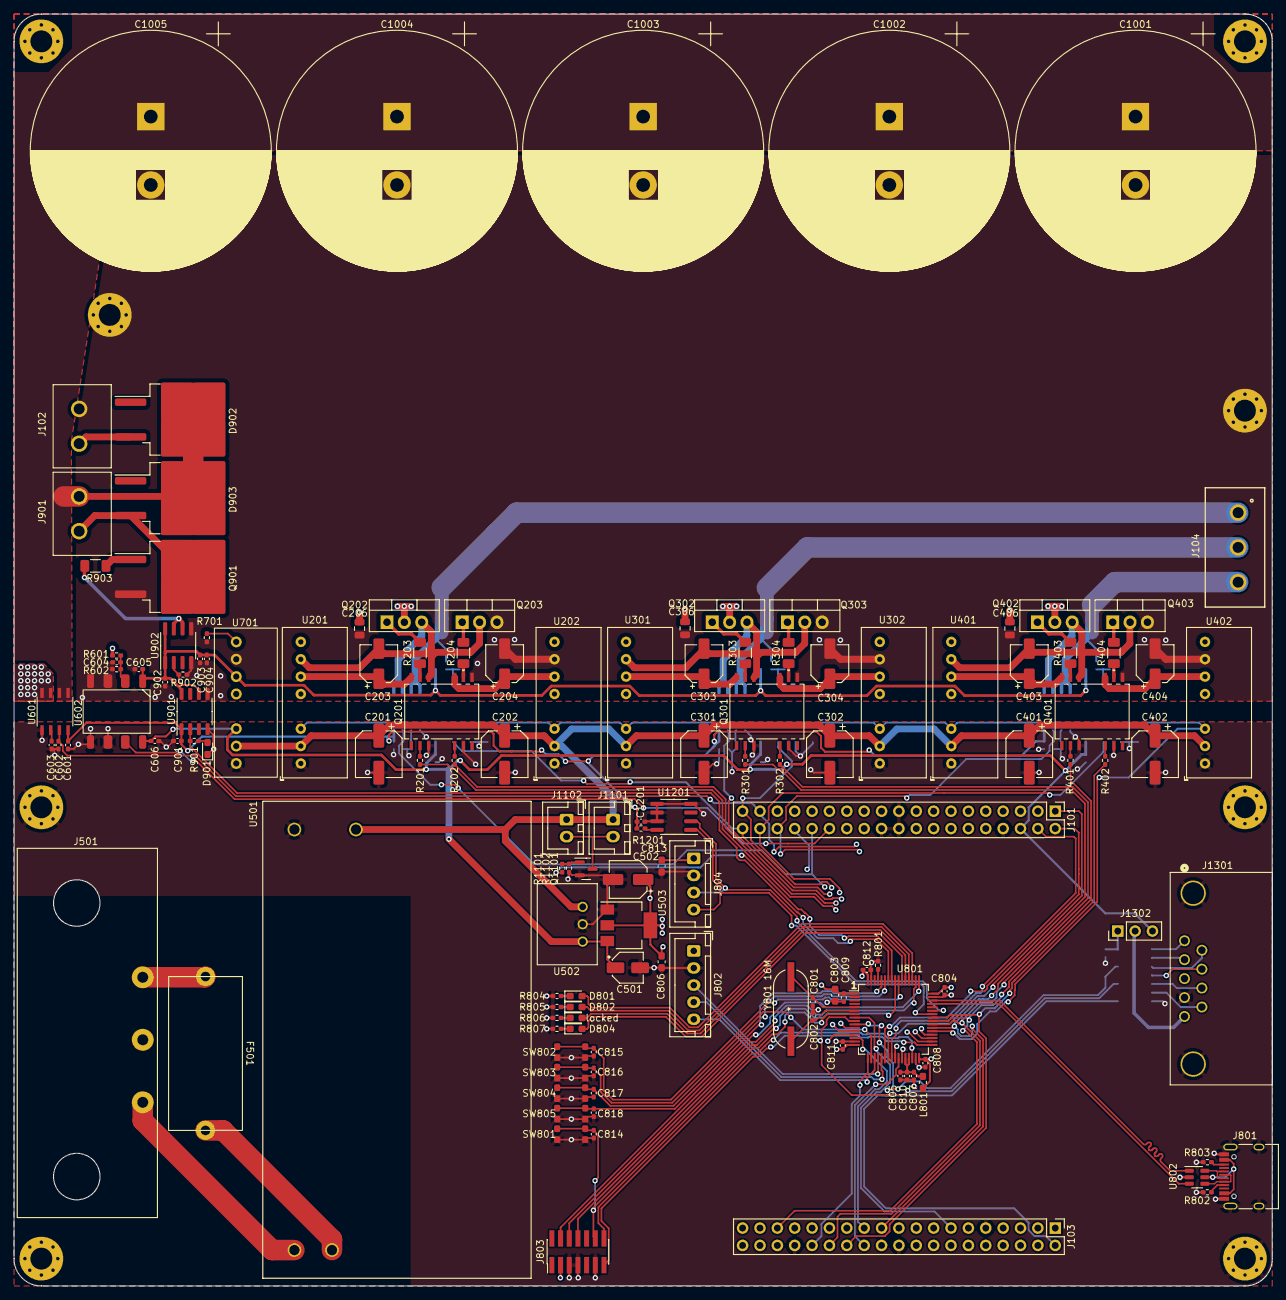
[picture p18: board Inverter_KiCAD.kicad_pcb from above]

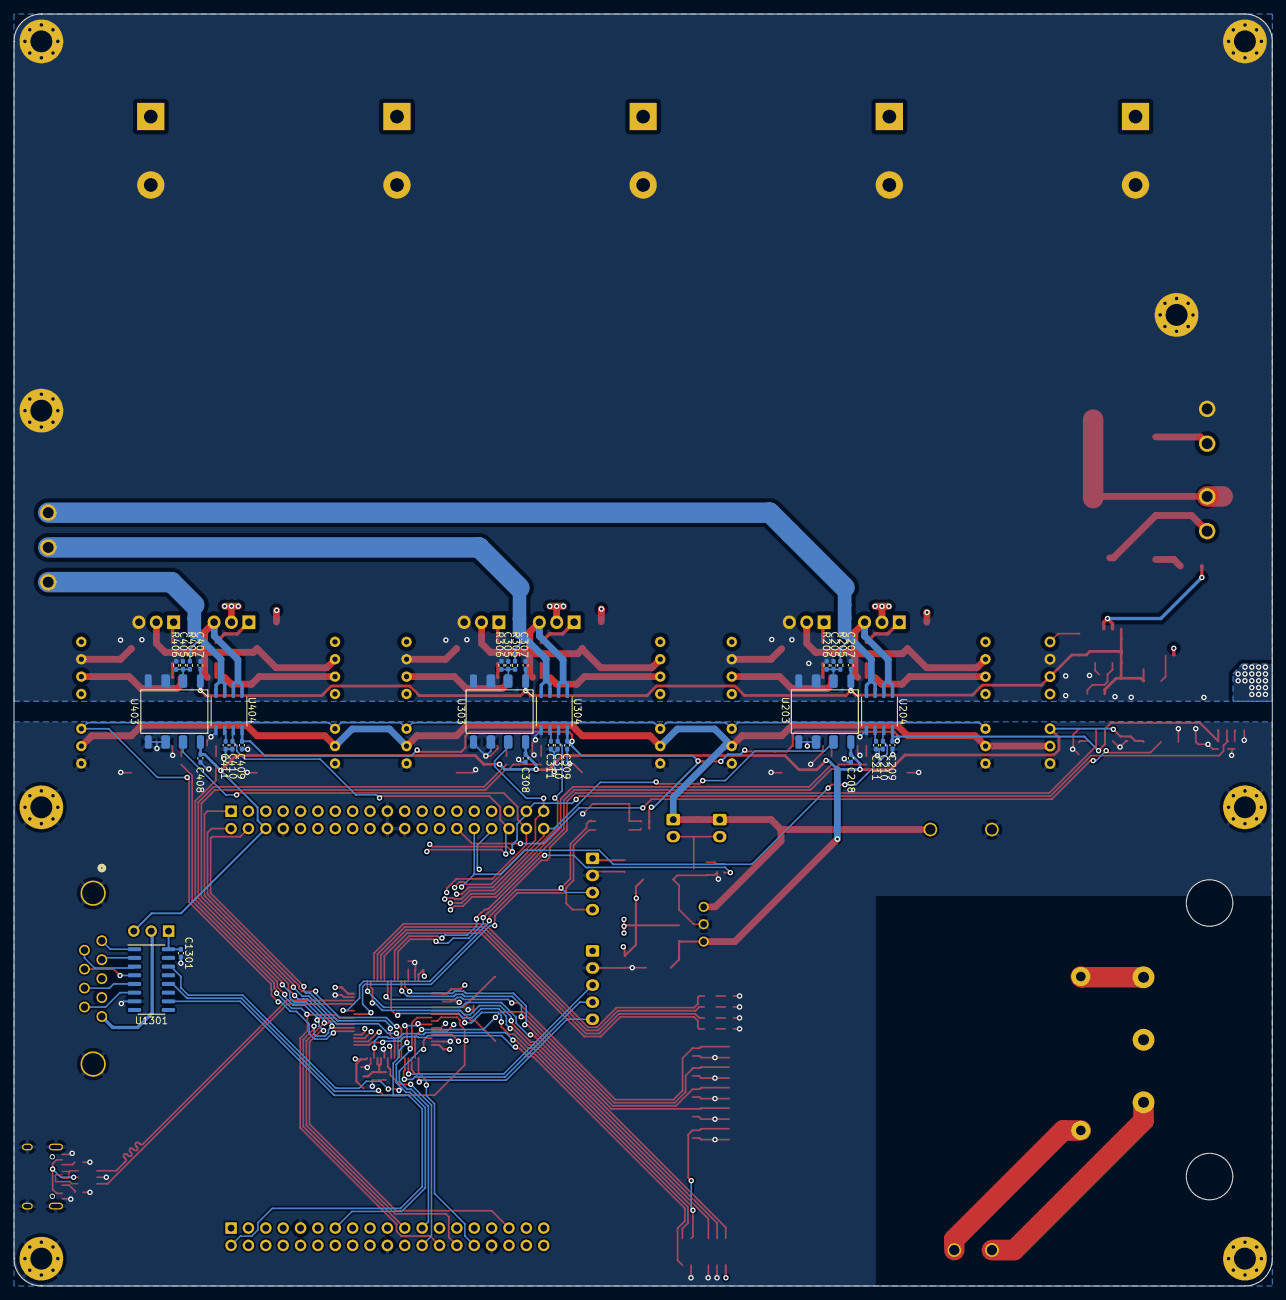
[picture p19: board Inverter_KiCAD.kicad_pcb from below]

Board: 4 copper layers, 184.0 x 186.0 mm, 176 parts (32 on the bottom side), 123 nets.

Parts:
C201, C202, C301, C302, C401, C402: 100u; CP_Elec_6.3x7.7
C203, C204, C303, C304, C403, C404, C502: 22u; CP_Elec_5x5.4
C205, C305, C405, C604: 10n; C_0402_1005Metric_Pad0.74x0.62mm_HandSolder
C206, C306, C406: 10u; C_0805_2012Metric
C207, C208, C307, C308, C407, C408, C605, C606, C804, C807, C808, C809, C810, C811, C812, C814, C815, C816, C817, C818, C901, C902, C1201, C1301: 100n; C_0402_1005Metric_Pad0.74x0.62mm_HandSolder
C209, C210, C211, C309, C310, C311, C409, C410, C411, C601, C602, C603: 4.7n; C_0402_1005Metric_Pad0.74x0.62mm_HandSolder
C501: 10u; CP_Elec_4x5.4
C801, C802: 18p; C_0402_1005Metric_Pad0.74x0.62mm_HandSolder
C803, C806, C813: 10u; C_0603_1608Metric_Pad1.08x0.95mm_HandSolder
C805, C903: 1u; C_0402_1005Metric_Pad0.74x0.62mm_HandSolder
C904: 1n; C_0402_1005Metric_Pad0.74x0.62mm_HandSolder
C1001, C1002, C1003, C1004, C1005: 1.5m; CP_Radial_D35.0mm_P10.00mm_SnapIn
D801, D802, D804: LED; LED_0603_1608Metric_Pad1.05x0.95mm_HandSolder
D901: Red; LED_0603_1608Metric_Pad1.05x0.95mm_HandSolder
D902, D903: VS-15TQ060S-M3; TO-263-2
F501: Fuse; 0031.8201
H101, H102, H103, H104, H105, H106, H107, H108: MountingHole_Pad; MountingHole_3.2mm_M3_Pad_Via
J101, J103: Conn_02x19_Odd_Even; PinHeader_2x19_P2.54mm_Vertical
J102, J901: Conn_01x02; 691311500102
J104: Conn_01x03; 691311500103
J501: PX0580-PC-12132
J801: USB_C_Receptacle_USB2.0; USB_C_Receptacle_HRO_TYPE-C-31-M-12
J802: Conn_01x05; JST_XH_B5B-XH-A_1x05_P2.50mm_Vertical
J803: Conn_ST_STDC14; PinHeader_2x07_P1.27mm_Vertical_SMD
J804: Conn_01x04; JST_XH_B4B-XH-A_1x04_P2.50mm_Vertical
J1101, J1102: Conn_01x02; JST_XH_B2B-XH-A_1x02_P2.50mm_Vertical
J1301: DE9_Receptacle_MountingHoles; 618009233821
J1302: Conn_01x03; PinHeader_1x03_P2.54mm_Vertical
L801: 39n; L_0603_1608Metric_Pad1.05x0.95mm_HandSolder
Q201, Q301, Q401: HCPL-315J-500E; SO-16_HCPL-315J_BRA
Q202, Q203, Q302, Q303, Q402, Q403: IRF540N; TO-220-3_Vertical
Q901: BUK9637-100E; TO-263-2
Q1101: SQ2310ES; SOT-23
R201, R202, R301, R302, R401, R402: 170; R_0402_1005Metric_Pad0.72x0.64mm_HandSolder
R203, R204, R303, R304, R403, R404: 30; R_1206_3216Metric_Pad1.30x1.75mm_HandSolder
R205, R305, R405, R601: 160k; R_0402_1005Metric_Pad0.72x0.64mm_HandSolder
R206, R306, R406, R602: 1k; R_0402_1005Metric_Pad0.72x0.64mm_HandSolder
R701: 27k; R_0402_1005Metric_Pad0.72x0.64mm_HandSolder
R801, R902, R1102: 10k; R_0402_1005Metric_Pad0.72x0.64mm_HandSolder
R802, R803: 5.1k; R_0402_1005Metric_Pad0.72x0.64mm_HandSolder
R804, R805, R806, R807: 340; R_0402_1005Metric_Pad0.72x0.64mm_HandSolder
R901: 100; R_0402_1005Metric_Pad0.72x0.64mm_HandSolder
R903: 5; R_1206_3216Metric_Pad1.30x1.75mm_HandSolder
R1101: 22; R_0402_1005Metric_Pad0.72x0.64mm_HandSolder
R1201: 200; R_0402_1005Metric_Pad0.72x0.64mm_HandSolder
SW801, SW802, SW803, SW804, SW805: SW_Push; 435451019820
U201, U202, U301, U302, U401, U402: MPRB2415S-6W; MPRB2415S
U203, U303, U403, U602: HCPL-7800-500E; DIP-8 Gull Wing
U204, U304, U404, U601: GO 10-SME/SP3; SOIC8-GO-SME&slash_SP3_LEM
U501: MP-LD30-23B12R2; MP-LD30-23B15R2
U502: 173010542; 173010578
U503: AZ1117-3.3; SOT-223-3_TabPin2
U701: 17791063215
U801: STM32G474RETx; LQFP-64_10x10mm_P0.5mm
U802: USBLC6-2SC6; SOT-23-6
U901: ACPL-077L; SO-8_3.9x4.9mm_P1.27mm
U902: TC1412; SOIC-8_3.9x4.9mm_P1.27mm
U1201: TCN75A; SOIC-8_3.9x4.9mm_P1.27mm
U1301: MAX3097ECSE+; SOIC-16_3.9x9.9mm_P1.27mm
Y801: 16M; ABLS-7.3728MHZ-CL-RESR-A-1-G-F
locked: LED; LED_0603_1608Metric_Pad1.05x0.95mm_HandSolder

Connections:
/5V: C207.1, C307.1, C407.1, C605.1, C902.1, C903.1, C904.1, U203.1 (VDD1), U303.1 (VDD1), U403.1 (VDD1), U602.1 (VDD1), U701.6 (Vout), U901.8 (VDD2), U902.1 (VDD), U902.8 (VDD)
/Arm_IRF540NBbF1/ARM_OUT: C303.2, Q301.14 (VEE), Q302.3 (S), Q303.2 (D), U301.7 (0V), U304.1 (IP+), U304.2 (IP+)
/Arm_IRF540NBbF1/Cmd_H: Q302.1 (G), R303.2
/Arm_IRF540NBbF1/Cmd_L: Q303.1 (G), R304.2
/Arm_IRF540NBbF1/Uref: C311.1, U304.6 (UREF)
/Arm_IRF540NBbF1/VCC_H: C303.1, Q301.16 (VCC), U301.6 (Vout)
/Arm_IRF540NBbF1/VCC_L: C304.1, Q301.11 (VCC), U302.6 (Vout)
/Arm_IRF540NBbF2/ARM_OUT: C403.2, Q401.14 (VEE), Q402.3 (S), Q403.2 (D), U401.7 (0V), U404.1 (IP+), U404.2 (IP+)
/Arm_IRF540NBbF2/Cmd_H: Q402.1 (G), R403.2
/Arm_IRF540NBbF2/Cmd_L: Q403.1 (G), R404.2
/Arm_IRF540NBbF2/Uref: C411.1, U404.6 (UREF)
/Arm_IRF540NBbF2/VCC_H: C403.1, Q401.16 (VCC), U401.6 (Vout)
/Arm_IRF540NBbF2/VCC_L: C404.1, Q401.11 (VCC), U402.6 (Vout)
/Arm_IRF540NBbF/ARM_OUT: C203.2, Q201.14 (VEE), Q202.3 (S), Q203.2 (D), U201.7 (0V), U204.1 (IP+), U204.2 (IP+)
/Arm_IRF540NBbF/Cmd_H: Q202.1 (G), R203.2
/Arm_IRF540NBbF/Cmd_L: Q203.1 (G), R204.2
/Arm_IRF540NBbF/Uref: C211.1, U204.6 (UREF)
/Arm_IRF540NBbF/VCC_H: C203.1, Q201.16 (VCC), U201.6 (Vout)
/Arm_IRF540NBbF/VCC_L: C204.1, Q201.11 (VCC), U202.6 (Vout)
/Bus_Imes: C602.1, J101.35, U601.7 (UOUT), U801.36 (PB14)
/Bus_V: J101.28, U602.7 (VOUT+), U801.34 (PB12)
/ENC_A: J103.13, U801.8 (PC0), U1301.14 (OutA)
/ENC_B: J101.32, U801.9 (PC1), U1301.12 (OutB)
/ENC_Z: J103.2, U801.10 (PC2), U1301.10 (OutZ)
/I2C_SCL: J804.3, U801.43 (PA9), U1201.2 (SCL)
/I2C_SDA: J804.4, U801.42 (PA8), U1201.1 (SDA)
/ISO_3V3: C209.1, C309.1, C409.1, C502.1, C601.1, C803.1, C804.1, C806.2, C808.1, C809.1, C811.1, C812.1, C813.1, C901.1, C1201.1, C1301.1, J802.1, J803.3 (VCC), J804.1, J1302.1, L801.1, R1201.2, U204.8 (UC), U304.8 (UC), U404.8 (UC), U503.2 (VO), U601.8 (UC), U801.1 (VBAT), U801.16 (VDD), U801.32 (VDD), U801.48 (VDD), U801.64 (VDD), U901.1 (VDD1), U1301.16 (VCC)
/ISO_5V: C208.1, C308.1, C408.1, C501.1, C606.1, J101.6, J1302.3, U203.8 (VDD2), U303.8 (VDD2), U403.8 (VDD2), U502.3 (5V), U503.3 (VI), U602.8 (VDD2), U701.3 (Ctrl)
/ISO_15V: C201.1, C202.1, C301.1, C302.1, C401.1, C402.1, J1101.1, J1102.1, U201.2 (Vin), U202.2 (Vin), U301.2 (Vin), U302.2 (Vin), U401.2 (Vin), U402.2 (Vin), U501.3 (+15V), U502.1 (VIN), U701.2 (Vin)
/ISO_GND: C201.2, C202.2, C208.2, C209.2, C210.2, C211.2, C301.2, C302.2, C308.2, C309.2, C310.2, C311.2, C401.2, C402.2, C408.2, C409.2, C410.2, C411.2, C501.2, C502.2, C601.2, C602.2, C603.2, C606.2, C801.1, C802.1, C803.2, C804.2, C805.2, C806.1, C807.2, C808.2, C809.2, C810.2, C811.2, C812.2, C813.2, C814.2, C815.2, C816.2, C817.2, C818.2, C901.2, C1201.2, C1301.2, D901.1 (K), H102.1, H103.1, H104.1, J101.8, J101.19, J101.20, J101.22, J103.9, J103.20, J103.32, J801.A1 (GND), J801.A12 (GND), J801.B1 (GND), J801.B12 (GND), J801.S1 (SHIELD), J802.2, J803.5 (GND), J803.7 (GND), J803.11 (GNDDetect), J804.2, J1301.4, J1301.10 (PAD), Q201.3 (Cathode), Q201.7 (Cathode), Q301.3 (Cathode), Q301.7 (Cathode), Q401.3 (Cathode), Q401.7 (Cathode), Q1101.2 (S), R801.2, R802.2, R803.2, R804.2, R805.2, R806.2, R807.2, R1102.2, SW801.2, SW802.2, SW803.2, SW804.2, SW805.2, U201.1 (GND), U202.1 (GND), U203.5 (GND2), U203.6 (VOUT-), U204.5 (GND), U301.1 (GND), U302.1 (GND), U303.5 (GND2), U303.6 (VOUT-), U304.5 (GND), U401.1 (GND), U402.1 (GND), U403.5 (GND2), U403.6 (VOUT-), U404.5 (GND), U501.4 (GND), U502.2 (GND), U503.1 (GND), U601.5 (GND), U602.5 (GND2), U602.6 (VOUT-), U701.1 (Vin_GND), U801.15 (VSS), U801.27 (VSSA), U801.31 (VSS), U801.47 (VSS), U801.63 (VSS), U802.2 (GND), U901.4 (GND1), U1201.4 (GND), U1201.5 (A2), U1201.6 (A1), U1201.7 (A0), U1301.7 (GND)
/ISO_PWM_Break: R901.1, U801.58 (PB5), U901.2 (In)
/ISO_PWM_FAN: R1101.2, U801.57 (PB4)
/MCU_STM32G474/D+: J801.A6 (D+), J801.B6 (D+), U802.6 (I/O1)
/MCU_STM32G474/D-: J801.A7 (D-), J801.B7 (D-), U802.4 (I/O2)
/MCU_STM32G474/ENC_BTN_A: J802.3, U801.20 (PA6)
/MCU_STM32G474/ENC_BTN_B: J802.4, U801.21 (PA7)
/MCU_STM32G474/ENC_BTN_P: J802.5, U801.19 (PA5)
/MCU_STM32G474/ISO_3V3A: C805.1, C807.1, C810.1, L801.2, U801.28 (VREF+), U801.29 (VDDA)
/MCU_STM32G474/NRST: C814.1, J803.12 (~RST), SW801.1, U801.7 (PG10)
/MCU_STM32G474/SWCLK: J803.6 (JCLK/SWCLK), U801.50 (PA14)
/MCU_STM32G474/SWDIO: J803.4 (JTMS/SWDIO), U801.49 (PA13)
/MCU_STM32G474/SWO: J803.8 (JTDO/SWO), U801.56 (PB3)
/MCU_STM32G474/Soft_NRST: C818.1, SW805.1, U801.60 (PB7)
/MCU_STM32G474/USB_DM: U801.45 (PA11), U802.3 (I/O2)
/MCU_STM32G474/USB_DP: U801.46 (PA12), U802.1 (I/O1)
/MCU_STM32G474/USR_BTN_1: C815.1, SW802.1, U801.55 (PD2)
/MCU_STM32G474/USR_BTN_2: C816.1, SW803.1, U801.18 (PA4)
/MCU_STM32G474/USR_BTN_3: C817.1, SW804.1, U801.59 (PB6)
/MCU_STM32G474/USR_LED_1: D801.2 (A), U801.51 (PA15)
/MCU_STM32G474/USR_LED_2: D802.2 (A), U801.52 (PC10)
/MCU_STM32G474/USR_LED_3: U801.53 (PC11), locked.2 (A)
/MCU_STM32G474/USR_LED_4: D804.2 (A), U801.54 (PC12)
/MCU_STM32G474/VCP_RX: J803.13 (VCP_RX), U801.33 (PB11)
/MCU_STM32G474/VCP_TX: J803.14 (VCP_TX), U801.30 (PB10)
/MCU_STM32G474/V_USB: J801.A4 (VBUS), J801.A9 (VBUS), J801.B4 (VBUS), J801.B9 (VBUS), U802.5 (VBUS)
/NUCLEO_NRST: J101.4, U801.24 (PB0)
/NUCLEO_RX: J101.2, U801.22 (PC4)
/NUCLEO_TX: J101.1, U801.23 (PC5)
/Pwr_En: U201.3 (Ctrl), U202.3 (Ctrl), U301.3 (Ctrl), U302.3 (Ctrl), U401.3 (Ctrl), U402.3 (Ctrl), U801.37 (PB15)
/U_Imes: C210.1, J101.30, U204.7 (UOUT), U801.13 (PA1)
/U_PWM_H: J103.23, R201.2, U801.14 (PA2)
/U_PWM_L: J103.30, R202.2, U801.17 (PA3)
/U_VPh: J101.38, U203.7 (VOUT+), U801.12 (PA0)
/U_output: J104.1, R205.1, U204.3 (IP-), U204.4 (IP-)
/VSupply_AB: C1001.1, C1002.1, C1003.1, C1004.1, C1005.1, D902.2 (K), D903.2 (K), J901.2, U601.1 (IP+), U601.2 (IP+)
/VSupply_BB: D902.3 (A), J102.1
/V_Imes: C310.1, J103.24, U304.7 (UOUT), U801.26 (PB2)
/V_PWM_H: J103.21, R301.2, U801.38 (PC6)
/V_PWM_L: J103.28, R302.2, U801.39 (PC7)
/V_VPh: J101.37, U303.7 (VOUT+), U801.11 (PC3)
/V_output: J104.2, R305.1, U304.3 (IP-), U304.4 (IP-)
/Vbus: C206.1, C306.1, C406.1, Q202.2 (D), Q302.2 (D), Q402.2 (D), R601.1, U601.3 (IP-), U601.4 (IP-)
/Vbus_Sense/Uref: C603.1, U601.6 (UREF)
/W_Imes: C410.1, J101.34, U404.7 (UOUT), U801.35 (PB13)
/W_PWM_H: J103.33, R401.2, U801.40 (PC8)
/W_PWM_L: J103.26, R402.2, U801.41 (PC9)
/W_VPh: J101.36, U403.7 (VOUT+), U801.25 (PB1)
/W_output: J104.3, R405.1, U404.3 (IP-), U404.4 (IP-)
/break/Break_Drain_Mosfet: D903.3 (A), J901.1, Q901.2 (D)
/break/PWM_Break: R902.1, U901.6 (Out), U902.2 (IN)
/break/PWM_Mosfet: R903.1, U902.6 (OUT), U902.7 (OUT)
/encoderMotor/A: J1301.1, U1301.1 (A)
/encoderMotor/B: J1301.6, U1301.3 (B)
/encoderMotor/VCC_Enc: J1301.5, J1302.2
/encoderMotor/Z: J1301.8, U1301.5 (Z)
/encoderMotor//A: J1301.2, U1301.2 (/A)
/encoderMotor//B: J1301.7, U1301.4 (/B)
/encoderMotor//Z: J1301.9, U1301.6 (/Z)
GND: C204.2, C205.2, C206.2, C207.2, C304.2, C305.2, C306.2, C307.2, C404.2, C405.2, C406.2, C407.2, C604.2, C605.2, C902.2, C903.2, C904.2, C1001.2, C1002.2, C1003.2, C1004.2, C1005.2, H105.1, H106.1, H107.1, H108.1, J102.2, Q201.9 (VEE), Q203.3 (S), Q301.9 (VEE), Q303.3 (S), Q401.9 (VEE), Q403.3 (S), Q901.3 (S), R206.2, R306.2, R406.2, R602.2, R701.2, R902.2, U202.7 (0V), U203.3 (VIN-), U203.4 (GND1), U302.7 (0V), U303.3 (VIN-), U303.4 (GND1), U402.7 (0V), U403.3 (VIN-), U403.4 (GND1), U602.3 (VIN-), U602.4 (GND1), U701.7 (Vout_Gnd), U901.5 (GND2), U902.4 (GND), U902.5 (GND)
unnamed: D801.1 (K), R804.1
unnamed: D802.1 (K), R805.1
unnamed: R806.1, locked.1 (K)
unnamed: D804.1 (K), R807.1
unnamed: D901.2 (A), R901.2
unnamed: F501.1, J501.3 (L)
unnamed: J501.1 (N), U501.1 (AC(L))
unnamed: J801.A5 (CC1), R802.1
unnamed: J801.B5 (CC2), R803.1
unnamed: J1101.2, J1102.2, Q1101.3 (D)
unnamed: Q201.2 (Anode), R201.1
unnamed: Q201.6 (Anode), R202.1
unnamed: Q201.10 (Vo), R204.1
unnamed: Q201.15 (Vo), R203.1
unnamed: Q301.2 (Anode), R301.1
unnamed: Q301.6 (Anode), R302.1
unnamed: Q301.10 (Vo), R304.1
unnamed: Q301.15 (Vo), R303.1
unnamed: Q401.2 (Anode), R401.1
unnamed: Q401.6 (Anode), R402.1
unnamed: Q401.10 (Vo), R404.1
unnamed: Q401.15 (Vo), R403.1
unnamed: Q901.1 (G), R903.2
unnamed: Q1101.1 (G), R1101.1, R1102.1
unnamed: C205.1, R205.2, R206.1, U203.2 (VIN+)
unnamed: C305.1, R305.2, R306.1, U303.2 (VIN+)
unnamed: C405.1, R405.2, R406.1, U403.2 (VIN+)
unnamed: F501.2, U501.2 (AC(N))
unnamed: C604.1, R601.2, R602.1, U602.2 (VIN+)
unnamed: R701.1, U701.8 (FB)
unnamed: R801.1, U801.61 (PB8)
unnamed: C801.2, U801.5 (PF0), Y801.2
unnamed: C802.2, U801.6 (PF1), Y801.1
unnamed: R1201.1, U1201.8 (VDD)

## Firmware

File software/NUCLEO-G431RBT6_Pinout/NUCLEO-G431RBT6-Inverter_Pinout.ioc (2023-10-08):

#MicroXplorer Configuration settings - do not modify
ADC1.Channel-2\#ChannelRegularConversion=ADC_CHANNEL_12
ADC1.CommonPathInternal=null|null|null|null
ADC1.IPParameters=Rank-2\#ChannelRegularConversion,Channel-2\#ChannelRegularConversion,SamplingTime-2\#ChannelRegularConversion,OffsetNumber-2\#ChannelRegularConversion,NbrOfConversionFlag,master,CommonPathInternal
ADC1.NbrOfConversionFlag=1
ADC1.OffsetNumber-2\#ChannelRegularConversion=ADC_OFFSET_NONE
ADC1.Rank-2\#ChannelRegularConversion=1
ADC1.SamplingTime-2\#ChannelRegularConversion=ADC_SAMPLETIME_2CYCLES_5
ADC1.master=1
ADC2.Channel-0\#ChannelRegularConversion=ADC_CHANNEL_6
ADC2.CommonPathInternal=null|null|null|null
ADC2.IPParameters=Rank-0\#ChannelRegularConversion,Channel-0\#ChannelRegularConversion,SamplingTime-0\#ChannelRegularConversion,OffsetNumber-0\#ChannelRegularConversion,NbrOfConversionFlag,CommonPathInternal
ADC2.NbrOfConversionFlag=1
ADC2.OffsetNumber-0\#ChannelRegularConversion=ADC_OFFSET_NONE
ADC2.Rank-0\#ChannelRegularConversion=1
ADC2.SamplingTime-0\#ChannelRegularConversion=ADC_SAMPLETIME_2CYCLES_5
CAD.formats=
CAD.pinconfig=
CAD.provider=
File.Version=6
KeepUserPlacement=false
Mcu.CPN=STM32G431RBT6
Mcu.Family=STM32G4
Mcu.IP0=ADC1
Mcu.IP1=ADC2
Mcu.IP2=NVIC
Mcu.IP3=RCC
Mcu.IP4=SYS
Mcu.IP5=TIM1
Mcu.IP6=TIM3
Mcu.IP7=USART2
Mcu.IP8=USART3
Mcu.IPNb=9
Mcu.Name=STM32G431R(6-8-B)Tx
Mcu.Package=LQFP64
Mcu.Pin0=PC13
Mcu.Pin1=PC14-OSC32_IN
Mcu.Pin10=PA1
Mcu.Pin11=PA2
Mcu.Pin12=PA3
Mcu.Pin13=PA4
Mcu.Pin14=PA5
Mcu.Pin15=PA6
Mcu.Pin16=PB0
Mcu.Pin17=PB1
Mcu.Pin18=PB13
Mcu.Pin19=PB14
Mcu.Pin2=PC15-OSC32_OUT
Mcu.Pin20=PB15
Mcu.Pin21=PC8
Mcu.Pin22=PA8
Mcu.Pin23=PA9
Mcu.Pin24=PA10
Mcu.Pin25=PA13
Mcu.Pin26=PA14
Mcu.Pin27=PC10
Mcu.Pin28=PC11
Mcu.Pin29=PD2
Mcu.Pin3=PF0-OSC_IN
Mcu.Pin30=PB3
Mcu.Pin31=VP_SYS_VS_Systick
Mcu.Pin32=VP_SYS_VS_DBSignals
Mcu.Pin33=VP_TIM1_VS_ClockSourceINT
Mcu.Pin4=PF1-OSC_OUT
Mcu.Pin5=PC0
Mcu.Pin6=PC1
Mcu.Pin7=PC2
Mcu.Pin8=PC3
Mcu.Pin9=PA0
Mcu.PinsNb=34
Mcu.ThirdPartyNb=0
Mcu.UserConstants=
Mcu.UserName=STM32G431RBTx
MxCube.Version=6.9.1
MxDb.Version=DB.6.0.91
NVIC.BusFault_IRQn=true\:0\:0\:false\:false\:true\:false\:false\:false
NVIC.DebugMonitor_IRQn=true\:0\:0\:false\:false\:true\:false\:false\:false
NVIC.ForceEnableDMAVector=true
NVIC.HardFault_IRQn=true\:0\:0\:false\:false\:true\:false\:false\:false
NVIC.MemoryManagement_IRQn=true\:0\:0\:false\:false\:true\:false\:false\:false
NVIC.NonMaskableInt_IRQn=true\:0\:0\:false\:false\:true\:false\:false\:false
NVIC.PendSV_IRQn=true\:0\:0\:false\:false\:true\:false\:false\:false
NVIC.PriorityGroup=NVIC_PRIORITYGROUP_4
NVIC.SVCall_IRQn=true\:0\:0\:false\:false\:true\:false\:false\:false
NVIC.SysTick_IRQn=true\:0\:0\:false\:false\:true\:false\:true\:false
NVIC.UsageFault_IRQn=true\:0\:0\:false\:false\:true\:false\:false\:false
PA0.GPIOParameters=GPIO_Label
PA0.GPIO_Label=BUS_V
PA0.Locked=true
PA0.Mode=IN1-Single-Ended
PA0.Signal=ADC2_IN1
PA1.GPIOParameters=GPIO_Label
PA1.GPIO_Label=U_Imes
PA1.Locked=true
PA1.Mode=IN2-Single-Ended
PA1.Signal=ADC1_IN2
PA10.GPIOParameters=GPIO_Label
PA10.GPIO_Label=W_PWM_H
PA10.Locked=true
PA10.Signal=S_TIM1_CH3
PA13.GPIOParameters=GPIO_Label
PA13.GPIO_Label=T_SWDIO
PA13.Locked=true
PA13.Mode=Trace_Asynchronous_SW
PA13.Signal=SYS_JTMS-SWDIO
PA14.GPIOParameters=GPIO_Label
PA14.GPIO_Label=T_SWCLK
PA14.Locked=true
PA14.Mode=Trace_Asynchronous_SW
PA14.Signal=SYS_JTCK-SWCLK
PA2.Mode=Asynchronous
PA2.Signal=USART2_TX
PA3.Locked=true
PA3.Mode=Asynchronous
PA3.Signal=USART2_RX
PA4.Signal=S_TIM3_CH2
PA5.GPIOParameters=GPIO_Label
PA5.GPIO_Label=USR_LED
PA5.Locked=true
PA5.Signal=GPIO_Output
PA6.Signal=S_TIM3_CH1
PA8.GPIOParameters=GPIO_Label
PA8.GPIO_Label=U_PWM_H
PA8.Locked=true
PA8.Signal=S_TIM1_CH1
PA9.GPIOParameters=GPIO_Label
PA9.GPIO_Label=V_PWM_H
PA9.Locked=true
PA9.Signal=S_TIM1_CH2
PB0.GPIOParameters=GPIO_Label
PB0.GPIO_Label=W_Imes
PB0.Locked=true
PB0.Mode=IN15-Single-Ended
PB0.Signal=ADC1_IN15
PB1.GPIOParameters=GPIO_Label
PB1.GPIO_Label=V_Imes
PB1.Locked=true
PB1.Mode=IN12-Single-Ended
PB1.Signal=ADC1_IN12
PB13.GPIOParameters=GPIO_Label
PB13.GPIO_Label=U_PWM_L
PB13.Locked=true
PB13.Mode=PWM Generation1 CH1 CH1N
PB13.Signal=TIM1_CH1N
PB14.GPIOParameters=GPIO_Label
PB14.GPIO_Label=V_PWM_L
PB14.Locked=true
PB14.Mode=PWM Generation2 CH2 CH2N
PB14.Signal=TIM1_CH2N
PB15.GPIOParameters=GPIO_Label
PB15.GPIO_Label=W_PWM_L
PB15.Locked=true
PB15.Mode=PWM Generation3 CH3 CH3N
PB15.Signal=TIM1_CH3N
PB3.GPIOParameters=GPIO_Label
PB3.GPIO_Label=T_SWO
PB3.Locked=true
PB3.Mode=Trace_Asynchronous_SW
PB3.Signal=SYS_JTDO-SWO
PC0.GPIOParameters=GPIO_Label
PC0.GPIO_Label=U_VPh
PC0.Locked=true
PC0.Mode=IN6-Single-Ended
PC0.Signal=ADC2_IN6
PC1.GPIOParameters=GPIO_Label
PC1.GPIO_Label=W_VPh
PC1.Locked=true
PC1.Mode=IN7-Single-Ended
PC1.Signal=ADC2_IN7
PC10.Locked=true
PC10.Mode=Asynchronous
PC10.Signal=USART3_TX
PC11.Locked=true
PC11.Mode=Asynchronous
PC11.Signal=USART3_RX
PC13.GPIOParameters=GPIO_Label
PC13.GPIO_Label=USR_BTN
PC13.Locked=true
PC13.Signal=GPXTI13
PC14-OSC32_IN.Locked=true
PC14-OSC32_IN.Mode=LSE-External-Oscillator
PC14-OSC32_IN.Signal=RCC_OSC32_IN
PC15-OSC32_OUT.Locked=true
PC15-OSC32_OUT.Mode=LSE-External-Oscillator
PC15-OSC32_OUT.Signal=RCC_OSC32_OUT
PC2.GPIOParameters=GPIO_Label
PC2.GPIO_Label=Bus_Imes
PC2.Mode=IN8-Single-Ended
PC2.Signal=ADC1_IN8
PC3.GPIOParameters=GPIO_Label
PC3.GPIO_Label=V_VPh
PC3.Locked=true
PC3.Mode=IN9-Single-Ended
PC3.Signal=ADC2_IN9
PC8.Signal=S_TIM3_CH3
PD2.GPIOParameters=GPIO_Label
PD2.GPIO_Label=NRST_SafetyUC
PD2.Locked=true
PD2.Signal=GPIO_Output
PF0-OSC_IN.Locked=true
PF0-OSC_IN.Mode=HSE-External-Oscillator
PF0-OSC_IN.Signal=RCC_OSC_IN
PF1-OSC_OUT.Locked=true
PF1-OSC_OUT.Mode=HSE-External-Oscillator
PF1-OSC_OUT.Signal=RCC_OSC_OUT
PinOutPanel.RotationAngle=0
ProjectManager.AskForMigrate=true
ProjectManager.BackupPrevious=false
ProjectManager.CompilerOptimize=6
ProjectManager.ComputerToolchain=false
ProjectManager.CoupleFile=true
ProjectManager.CustomerFirmwarePackage=
ProjectManager.DefaultFWLocation=true
ProjectManager.DeletePrevious=true
ProjectManager.DeviceId=STM32G431RBTx
ProjectManager.FirmwarePackage=STM32Cube FW_G4 V1.5.1
ProjectManager.FreePins=false
ProjectManager.HalAssertFull=false
ProjectManager.HeapSize=0x200
ProjectManager.KeepUserCode=true
ProjectManager.LastFirmware=true
ProjectManager.LibraryCopy=1
ProjectManager.MainLocation=Core/Src
ProjectManager.NoMain=false
ProjectManager.PreviousToolchain=
ProjectManager.ProjectBuild=false
ProjectManager.ProjectFileName=NUCLEO-G431RBT6-Inverter_Pinout.ioc
ProjectManager.ProjectName=NUCLEO-G431RBT6-Inverter_Pinout
ProjectManager.ProjectStructure=
ProjectManager.RegisterCallBack=
ProjectManager.StackSize=0x400
ProjectManager.TargetToolchain=STM32CubeIDE
ProjectManager.ToolChainLocation=
ProjectManager.UAScriptAfterPath=
ProjectManager.UAScriptBeforePath=
ProjectManager.UnderRoot=true
ProjectManager.functionlistsort=1-SystemClock_Config-RCC-false-HAL-false,2-MX_GPIO_Init-GPIO-false-HAL-true,3-MX_ADC1_Init-ADC1-false-HAL-true,4-MX_ADC2_Init-ADC2-false-HAL-true,5-MX_TIM1_Init-TIM1-false-HAL-true,6-MX_USART2_UART_Init-USART2-false-HAL-true,7-MX_USART3_UART_Init-USART3-false-HAL-true,8-MX_TIM3_Init-TIM3-false-HAL-true
RCC.ADC12Freq_Value=170000000
RCC.AHBFreq_Value=170000000
RCC.APB1Freq_Value=170000000
RCC.APB1TimFreq_Value=170000000
RCC.APB2Freq_Value=170000000
RCC.APB2TimFreq_Value=170000000
RCC.CRSFreq_Value=48000000
RCC.CortexFreq_Value=170000000
RCC.EXTERNAL_CLOCK_VALUE=12288000
RCC.FCLKCortexFreq_Value=170000000
RCC.FDCANFreq_Value=170000000
RCC.FamilyName=M
RCC.HCLKFreq_Value=170000000
RCC.HSE_VALUE=24000000
RCC.HSI48_VALUE=48000000
RCC.HSI_VALUE=16000000
RCC.I2C1Freq_Value=170000000
RCC.I2C2Freq_Value=170000000
RCC.I2C3Freq_Value=170000000
RCC.I2SFreq_Value=170000000
RCC.IPParameters=ADC12Freq_Value,AHBFreq_Value,APB1Freq_Value,APB1TimFreq_Value,APB2Freq_Value,APB2TimFreq_Value,CRSFreq_Value,CortexFreq_Value,EXTERNAL_CLOCK_VALUE,FCLKCortexFreq_Value,FDCANFreq_Value,FamilyName,HCLKFreq_Value,HSE_VALUE,HSI48_VALUE,HSI_VALUE,I2C1Freq_Value,I2C2Freq_Value,I2C3Freq_Value,I2SFreq_Value,LPTIM1Freq_Value,LPUART1Freq_Value,LSCOPinFreq_Value,LSI_VALUE,MCO1PinFreq_Value,PLLM,PLLN,PLLPoutputFreq_Value,PLLQoutputFreq_Value,PLLRCLKFreq_Value,PWRFreq_Value,RNGFreq_Value,RTCClockSelection,RTCFreq_Value,SAI1Freq_Value,SYSCLKFreq_VALUE,SYSCLKSource,UART4Freq_Value,USART1Freq_Value,USART2Freq_Value,USART3Freq_Value,USBFreq_Value,VCOInputFreq_Value,VCOOutputFreq_Value
RCC.LPTIM1Freq_Value=170000000
RCC.LPUART1Freq_Value=170000000
RCC.LSCOPinFreq_Value=32000
RCC.LSI_VALUE=32000
RCC.MCO1PinFreq_Value=16000000
RCC.PLLM=RCC_PLLM_DIV4
RCC.PLLN=85
RCC.PLLPoutputFreq_Value=170000000
RCC.PLLQoutputFreq_Value=170000000
RCC.PLLRCLKFreq_Value=170000000
RCC.PWRFreq_Value=170000000
RCC.RNGFreq_Value=170000000
RCC.RTCClockSelection=RCC_RTCCLKSOURCE_LSE
RCC.RTCFreq_Value=32768
RCC.SAI1Freq_Value=170000000
RCC.SYSCLKFreq_VALUE=170000000
RCC.SYSCLKSource=RCC_SYSCLKSOURCE_PLLCLK
RCC.UART4Freq_Value=170000000
RCC.USART1Freq_Value=170000000
RCC.USART2Freq_Value=170000000
RCC.USART3Freq_Value=170000000
RCC.USBFreq_Value=170000000
RCC.VCOInputFreq_Value=4000000
RCC.VCOOutputFreq_Value=340000000
SH.GPXTI13.0=GPIO_EXTI13
SH.GPXTI13.ConfNb=1
SH.S_TIM1_CH1.0=TIM1_CH1,PWM Generation1 CH1 CH1N
SH.S_TIM1_CH1.ConfNb=1
SH.S_TIM1_CH2.0=TIM1_CH2,PWM Generation2 CH2 CH2N
SH.S_TIM1_CH2.ConfNb=1
SH.S_TIM1_CH3.0=TIM1_CH3,PWM Generation3 CH3 CH3N
SH.S_TIM1_CH3.ConfNb=1
SH.S_TIM3_CH1.0=TIM3_CH1,Xored_Inputs_Hall_Sensor_Interface
SH.S_TIM3_CH1.ConfNb=1
SH.S_TIM3_CH2.0=TIM3_CH2,Xored_Inputs_Hall_Sensor_Interface
SH.S_TIM3_CH2.ConfNb=1
SH.S_TIM3_CH3.0=TIM3_CH3,Xored_Inputs_Hall_Sensor_Interface
SH.S_TIM3_CH3.ConfNb=1
TIM1.Channel-PWM\ Generation1\ CH1\ CH1N=TIM_CHANNEL_1
TIM1.Channel-PWM\ Generation2\ CH2\ CH2N=TIM_CHANNEL_2
TIM1.Channel-PWM\ Generation3\ CH3\ CH3N=TIM_CHANNEL_3
TIM1.CounterMode=TIM_COUNTERMODE_CENTERALIGNED1
TIM1.DeadTime=0
TIM1.IPParameters=Channel-PWM Generation1 CH1 CH1N,Channel-PWM Generation2 CH2 CH2N,Channel-PWM Generation3 CH3 CH3N,PeriodNoDither,Prescaler,CounterMode,DeadTime
TIM1.PeriodNoDither=1024-1
TIM1.Prescaler=9-1
USART2.IPParameters=VirtualMode-Asynchronous
USART2.VirtualMode-Asynchronous=VM_ASYNC
USART3.IPParameters=VirtualMode-Asynchronous
USART3.VirtualMode-Asynchronous=VM_ASYNC
VP_SYS_VS_DBSignals.Mode=DisableDeadBatterySignals
VP_SYS_VS_DBSignals.Signal=SYS_VS_DBSignals
VP_SYS_VS_Systick.Mode=SysTick
VP_SYS_VS_Systick.Signal=SYS_VS_Systick
VP_TIM1_VS_ClockSourceINT.Mode=Internal
VP_TIM1_VS_ClockSourceINT.Signal=TIM1_VS_ClockSourceINT
board=NUCLEO-G431RB
boardIOC=true
isbadioc=false

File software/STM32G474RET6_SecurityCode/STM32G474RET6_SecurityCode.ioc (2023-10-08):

#MicroXplorer Configuration settings - do not modify
ADC1.Channel-0\#ChannelRegularConversion=ADC_CHANNEL_1
ADC1.CommonPathInternal=null|null|null|null
ADC1.IPParameters=Rank-0\#ChannelRegularConversion,Channel-0\#ChannelRegularConversion,SamplingTime-0\#ChannelRegularConversion,OffsetNumber-0\#ChannelRegularConversion,NbrOfConversionFlag,master,CommonPathInternal
ADC1.NbrOfConversionFlag=1
ADC1.OffsetNumber-0\#ChannelRegularConversion=ADC_OFFSET_NONE
ADC1.Rank-0\#ChannelRegularConversion=1
ADC1.SamplingTime-0\#ChannelRegularConversion=ADC_SAMPLETIME_2CYCLES_5
ADC1.master=1
ADC2.Channel-0\#ChannelRegularConversion=ADC_CHANNEL_9
ADC2.CommonPathInternal=null|null|null|null
ADC2.IPParameters=Rank-0\#ChannelRegularConversion,Channel-0\#ChannelRegularConversion,SamplingTime-0\#ChannelRegularConversion,OffsetNumber-0\#ChannelRegularConversion,NbrOfConversionFlag,CommonPathInternal
ADC2.NbrOfConversionFlag=1
ADC2.OffsetNumber-0\#ChannelRegularConversion=ADC_OFFSET_NONE
ADC2.Rank-0\#ChannelRegularConversion=1
ADC2.SamplingTime-0\#ChannelRegularConversion=ADC_SAMPLETIME_2CYCLES_5
ADC3.Channel-0\#ChannelRegularConversion=ADC_CHANNEL_1
ADC3.CommonPathInternal=null|null|null|null
ADC3.IPParameters=Rank-0\#ChannelRegularConversion,Channel-0\#ChannelRegularConversion,SamplingTime-0\#ChannelRegularConversion,OffsetNumber-0\#ChannelRegularConversion,NbrOfConversionFlag,master,CommonPathInternal
ADC3.NbrOfConversionFlag=1
ADC3.OffsetNumber-0\#ChannelRegularConversion=ADC_OFFSET_NONE
ADC3.Rank-0\#ChannelRegularConversion=1
ADC3.SamplingTime-0\#ChannelRegularConversion=ADC_SAMPLETIME_2CYCLES_5
ADC3.master=1
ADC4.Channel-0\#ChannelRegularConversion=ADC_CHANNEL_3
ADC4.CommonPathInternal=null|null|null|null
ADC4.IPParameters=Rank-0\#ChannelRegularConversion,Channel-0\#ChannelRegularConversion,SamplingTime-0\#ChannelRegularConversion,OffsetNumber-0\#ChannelRegularConversion,NbrOfConversionFlag,CommonPathInternal
ADC4.NbrOfConversionFlag=1
ADC4.OffsetNumber-0\#ChannelRegularConversion=ADC_OFFSET_NONE
ADC4.Rank-0\#ChannelRegularConversion=1
ADC4.SamplingTime-0\#ChannelRegularConversion=ADC_SAMPLETIME_47CYCLES_5
CAD.formats=
CAD.pinconfig=
CAD.provider=
FREERTOS.HEAP_NUMBER=4
FREERTOS.IPParameters=Tasks01,configUSE_NEWLIB_REENTRANT,HEAP_NUMBER,configTOTAL_HEAP_SIZE,configTICK_RATE_HZ,configENABLE_FPU,configLIBRARY_MAX_SYSCALL_INTERRUPT_PRIORITY,configMAX_PRIORITIES,configLIBRARY_LOWEST_INTERRUPT_PRIORITY
FREERTOS.Tasks01=defaultTask,0,128,StartDefaultTask,Default,NULL,Dynamic,NULL,NULL
FREERTOS.configENABLE_FPU=1
FREERTOS.configLIBRARY_LOWEST_INTERRUPT_PRIORITY=15
FREERTOS.configLIBRARY_MAX_SYSCALL_INTERRUPT_PRIORITY=5
FREERTOS.configMAX_PRIORITIES=32
FREERTOS.configTICK_RATE_HZ=1000
FREERTOS.configTOTAL_HEAP_SIZE=16384
FREERTOS.configUSE_NEWLIB_REENTRANT=1
File.Version=6
GPIO.groupedBy=Group By Peripherals
I2C2.IPParameters=Timing
I2C2.Timing=0x30A0A7FB
KeepUserPlacement=false
Mcu.CPN=STM32G474RET3
Mcu.Family=STM32G4
Mcu.IP0=ADC1
Mcu.IP1=ADC2
Mcu.IP10=SYS
Mcu.IP11=TIM1
Mcu.IP12=TIM3
Mcu.IP13=TIM8
Mcu.IP14=TIM15
Mcu.IP15=TIM16
Mcu.IP16=TIM17
Mcu.IP17=USART1
Mcu.IP18=USART3
Mcu.IP19=USB
Mcu.IP2=ADC3
Mcu.IP20=USB_DEVICE
Mcu.IP3=ADC4
Mcu.IP4=CORDIC
Mcu.IP5=FMAC
Mcu.IP6=FREERTOS
Mcu.IP7=I2C2
Mcu.IP8=NVIC
Mcu.IP9=RCC
Mcu.IPNb=21
Mcu.Name=STM32G474R(B-C-E)Tx
Mcu.Package=LQFP64
Mcu.Pin0=PC13
Mcu.Pin1=PC14-OSC32_IN
Mcu.Pin10=PA0
Mcu.Pin11=PA1
Mcu.Pin12=PA2
Mcu.Pin13=PA3
Mcu.Pin14=PA4
Mcu.Pin15=PA5
Mcu.Pin16=PA6
Mcu.Pin17=PA7
Mcu.Pin18=PC4
Mcu.Pin19=PC5
Mcu.Pin2=PC15-OSC32_OUT
Mcu.Pin20=PB0
Mcu.Pin21=PB1
Mcu.Pin22=PB2
Mcu.Pin23=PB10
Mcu.Pin24=PB11
Mcu.Pin25=PB12
Mcu.Pin26=PB13
Mcu.Pin27=PB14
Mcu.Pin28=PC6
Mcu.Pin29=PC7
Mcu.Pin3=PF0-OSC_IN
Mcu.Pin30=PC8
Mcu.Pin31=PC9
Mcu.Pin32=PA8
Mcu.Pin33=PA9
Mcu.Pin34=PA11
Mcu.Pin35=PA12
Mcu.Pin36=PA13
Mcu.Pin37=PA14
Mcu.Pin38=PA15
Mcu.Pin39=PC10
Mcu.Pin4=PF1-OSC_OUT
Mcu.Pin40=PC11
Mcu.Pin41=PC12
Mcu.Pin42=PD2
Mcu.Pin43=PB3
Mcu.Pin44=PB4
Mcu.Pin45=PB5
Mcu.Pin46=PB6
Mcu.Pin47=PB7
Mcu.Pin48=VP_CORDIC_VS_CORDIC
Mcu.Pin49=VP_FMAC_VS_FMAC
Mcu.Pin5=PG10-NRST
Mcu.Pin50=VP_FREERTOS_VS_CMSIS_V1
Mcu.Pin51=VP_SYS_VS_tim6
Mcu.Pin52=VP_TIM1_VS_ClockSourceINT
Mcu.Pin53=VP_TIM8_VS_ClockSourceINT
Mcu.Pin54=VP_TIM15_VS_ClockSourceINT
Mcu.Pin55=VP_TIM16_VS_ClockSourceINT
Mcu.Pin56=VP_TIM17_VS_ClockSourceINT
Mcu.Pin57=VP_USB_DEVICE_VS_USB_DEVICE_CDC_FS
Mcu.Pin6=PC0
Mcu.Pin7=PC1
Mcu.Pin8=PC2
Mcu.Pin9=PC3
Mcu.PinsNb=58
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

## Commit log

2023-04-25 assigments footprints
    [Arm_IRF540NBbF.kicad_sch, Vbus_Sense.kicad_sch, pwrSupply.kicad_sch]
2023-04-25 update schematic
    [Arm_IRF540NBbF.kicad_sch, Inverter_KiCAD.kicad_sch, Vbus_Sense.kicad_sch, pwrSupply.kicad_sch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]
2023-04-27 add break
    [Arm_IRF540NBbF.kicad_sch, Inverter_KiCAD.kicad_pcb, Inverter_KiCAD.kicad_sch, MCU_STM32G474.kicad_sch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]
2023-04-28 start schematic Nucleo board
    [Arm_IRF540NBbF.kicad_sch, Inverter_KiCAD.kicad_sch, Vbus_Sense.kicad_sch, break.kicad_sch]
2023-04-29 clear schematic errors
    [Arm_IRF540NBbF.kicad_sch, Inverter_KiCAD.kicad_pcb, Inverter_KiCAD.kicad_sch, MCU_STM32G474.kicad_sch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]
2023-05-01 end of sch, start pcb
    [Arm_IRF540NBbF.kicad_sch, FAN.kicad_sch, Inverter_KiCAD.kicad_pcb, Inverter_KiCAD.kicad_sch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]
2023-05-04 rooting done
    [Arm_IRF540NBbF.kicad_sch, Inverter_KiCAD.kicad_pcb, Inverter_KiCAD.kicad_sch, MCU_STM32G474.kicad_sch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]
2023-05-10 update KiCAD 3D
    [Inverter_KiCAD.kicad_pcb]
2023-06-13 change pcb
    [Inverter_KiCAD.kicad_pcb, MCU_STM32G474.kicad_sch, pwrSupplyFiltering.kicad_sch]
2023-06-13 apply changes
    [Inverter_KiCAD.kicad_pcb, Inverter_KiCAD.kicad_sch, break.kicad_sch, pwrSupply.kicad_sch]
2023-06-27 Update KiCAD
    [Inverter_KiCAD.csv, Inverter_KiCAD.kicad_sch]
2023-06-27 change pbs
    [Inverter_KiCAD.kicad_pcb, Inverter_KiCAD.kicad_sch, pwrSupplyFiltering.kicad_sch]
2023-07-11 v0 PCB
    [Arm_IRF540NBbF.kicad_sch, Inverter_KiCAD-B_Cu.gbr, Inverter_KiCAD-B_Mask.gbr, Inverter_KiCAD-B_Paste.gbr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]
2023-07-19 soldering done, start test, power supply ok
    [Inverter_KiCAD-bottom-pos.csv, Inverter_KiCAD-top-pos.csv, Inverter_KiCAD-top-pos_placed.ods]
2023-08-31 update pcb
    [20230830_1341_Inverter_KiCAD.csv, Arm_IRF540NBbF.kicad_sch, FAN.kicad_sch, Inverter_KiCAD.csv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]
2023-09-06 add command sheet
    [MCU_STM32G474.kicad_sch, components.ods, encoderMotor.kicad_sch, wurth_projet_inverter_commande.ods]
2023-09-06 add eve/ese components
    [components.ods, wurth_projet_inverter_commande.ods]
2023-09-18 add G474RE base project
    [Inverter_KiCAD-B_Cu.gbr, Inverter_KiCAD-B_Mask.gbr, Inverter_KiCAD-B_Paste.gbr, Inverter_KiCAD-B_Silkscreen.gbr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]
2023-09-30 test on pcb v1
2023-11-06 change folders
    [20230830_1341_Inverter_KiCAD.csv, Arm_IRF540NBbF.kicad_sch, FAN.kicad_sch, Inverter_KiCAD-B_Cu.gbr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]
